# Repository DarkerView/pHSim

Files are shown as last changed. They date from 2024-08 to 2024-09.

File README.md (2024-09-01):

# An Open Source pH Probe Simulator
pH measurement is a quirky and often frustrating technology. Usually working well, they can go wrong in so many ways. With dozens upon dozens of pH probes in service on the cultivation pads I have now spent a few years attempting to discover all of the ways a pH measurement can go bad.

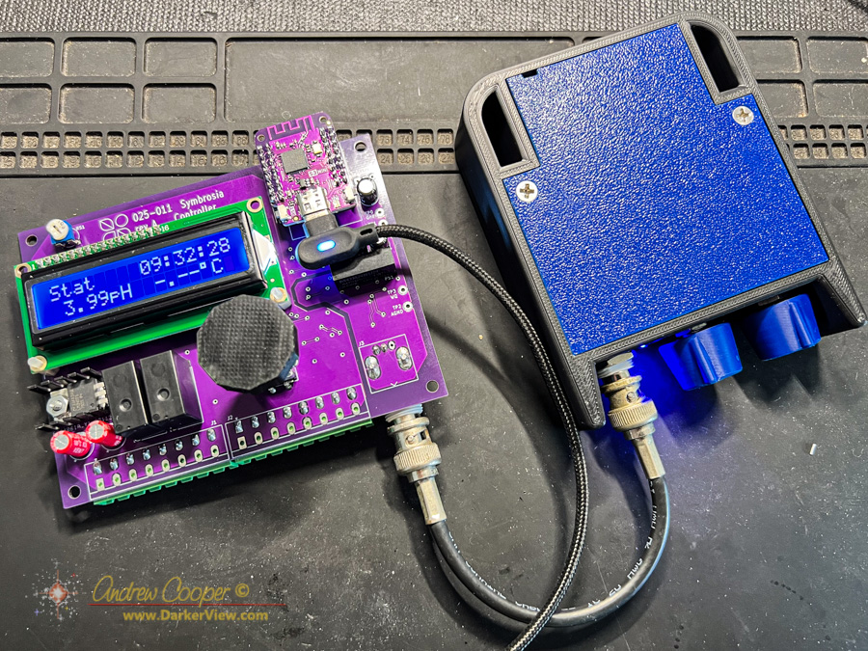
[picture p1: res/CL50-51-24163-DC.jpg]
pH Simulator in use testing a PBR controller


A voltage generated by [ion exchange across a glass membrane](https://atlas-scientific.com/blog/how-does-a-ph-probe-work/) is the magic that makes a pH probe work, simply measure the voltage and you can measure the [hydrogen ion activity of a solution](https://en.wikipedia.org/wiki/PH). The result is a number from 0 to 14, with numbers less than seven being acid, and numbers above seven being basic. Most life, such as healthy algae require conditions close to 7, or neutral, too acid or too basic and everything dies.

While the [voltage generated by the movement of hydrogen ions](https://www.hamiltoncompany.com/process-analytics/ph-and-orp-knowledge/ph-probe-operation-principles) is reasonably large, plus or minus half a volt, it generates only a miniscule current, a few nanoamps. This tiny current makes pH a [challenge to measure](https://en.wikipedia.org/wiki/PH_meter), requiring careful circuitry design in the pH meter. The small current also makes the signal easy to disrupt, a corroded contact, a little salt in a connector, or a damaged cable and it so easily goes awry.

The issue is usually a bad probe, though sometimes it is not. Corroded connectors are a common issue around salt water. In one case I had a cheap, and noisy power supply corrupting the readings. The other issue I face is probes that cannot be removed from the bioreactors once the reactor is full of a thousand liters of saltwater and algae. Thus confirming a bad probe versus another issue is even more critical.

Another problem has popped up on me… When the cultivation folks attempt to re-calibrate a failing probe it can result in bad calibration values entered into the pH instrument even once the offending probe has been replaced. Most instruments do not provide a way to view or reset these bad values. The result is even stranger behavior of the system and a very confused operator, then an equally confused engineer who gets called out to fix it.

My answer to these issues was to make myself a pH simulator, a little box that simulates an ideal pH probe. The actual device is electrically very, very simple… Some voltage references and a few resistors to simulate the voltages of a good pH probe.

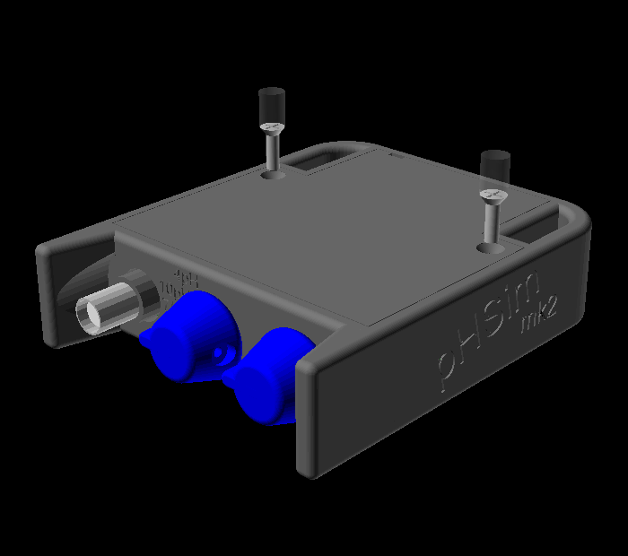
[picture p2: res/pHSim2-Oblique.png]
pH Simulator model


With this simulator I can disconnect the probe and test the pH meter separately, or recalibrate the instrument against an ideal simulated pH probe. The result is easy confirmation of a bad probe, a bad pH meter, or bad cabling. The simulator is also the ideal tool for testing or fixing a pH meter.

While the circuit design may be quite simple, it becomes a fun exercise to design a usable solution around it. First is to house the circuit in a rugged case that can withstand being thown in a toolbag or bounced off the concrete. This case is of course 3D printed from ABS plastic resulting in a solid housing that can take a bit of abuse. Add a proper printed circuit board and you have a neat solution that is pretty close to a commercial product.

No this device does not replace the need to calibrate with the actual pH probe you will be using.  This is an ideal probe, the real pH probe you will be using is less than ideal, compensating for that is what pH calibration is about.

Yes, commercially available pH simulators are out there, [for a thousand dollars](https://www.thomassci.com/Instruments/Electrodes-pH/_/pH-Simulator) or more. Aquaculture operations are quite often low budget startups, so low cost alternatives for useful tools make sense. Thus I am publishing the plans for the unit I originally designed and constructed for my own use.

I have chosen to release the device as a [Creative Commons non-commercial license CC BY-NC 4.0](/LICENSE.md), as this prohibits others from selling or profiting from the device but allows anyone to copy and use as long as they do not sell it for a profit.

As PCB’s are surprisingly cheap these days I have had a small stack of boards made and intend to give a few away to some folks I work with around [NELHA](https://nelha.hawaii.gov/). If you are interested in a PCB, or a kit of parts feel free to contact me.

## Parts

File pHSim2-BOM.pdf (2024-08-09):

# pHSim2 Bill of Materials

Item Description | Manuf | Part | Distributor | Cost | Qty | Exp
C1 | | Nichicon | UHV1V101MED | Digikey | $0.291 | 1 | $0.29
Würth Elektronik 860010573007 | Digikey | $0.150
| | Kemet | C1206C103M5RAC7800 | Digikey | $0.102 | 4 | $0.41
Würth Elektronik 885012208081 | Digikey | $0.115
| | Stackpole | CML1206X7R103KT50V | Digikey | $0.120
| | Yageo | CC1206KRX7R9BB103 | Digikey | $0.138
D1 | | Diodes Inc | S1A-13-F | Digikey | $0.172 | 1 | $0.17
| | Vishay | S1A-E3 | Digikey | $0.248
D2 | Würth Elektronik 151033BS03000 | Digikey | $0.260 | 1 | $0.26
| | Inolux | INL-3AB30 | Digikey | $0.279
J3 | | TE Connect | CONBNC002 | Digikey | $2.120 | 1 | $2.12
| | Adam | RF1-01K-D-00-50-BK-HDW | Digikey | $2.340
| | Stackpole | RMCF1206FT10K0 | Digikey | $0.024 | 4 | $0.10
| | Bourns | CR1206-FX-1002ELF | Digikey | $0.028
| | Yageo | RC1206FR-0710KL | Digikey | $0.038
| | Vishay Dale | CRCW120610K0FKEA | Digikey | $0.048
| | Stackpole | RNCP1206FTD1K00 | Digikey | $0.024 | 3 | $0.07
| | Bourns | CR1206-FX-1001ELF | Digikey | $0.028
| | Yageo | RC1206FR-071KL | Digikey | $0.038
| | Vishay Dale | CRCW12061K00FKEBC | Digikey | $0.048
R8, R9 | | Bourns | PV36W102C01B00 | Digikey | $1.550 | 2 | $3.10
| | TT Electronics | 67YR1KLF | Digikey | $1.690
| | Bourns | 3296Y-1-102LF | Digikey | $2.130
R10, R11 | | Stackpole | RMCF1206FT330R | Digikey | $0.024 | 2 | $0.05
| | Yageo | RC1206FR-07330RL | Digikey | $0.038
| | Bourns | CR1206-FX-3300ELF | Digikey | $0.044
| | Vishay Dale | CRCW1206330RFKEAC | Digikey | $0.045
R12, R13 | | Stackpole | RMCF1206FT20K0 | Digikey | $0.024 | 2 | $0.05
| | Bourns | CR1206-FX-2002ELF | Digikey | $0.028
| | Yageo | RC1206FR-0720KL | Digikey | $0.038
| | Vishay Dale | CRCW120620K0FKEAC | Digikey | $0.045
R14 | 10kΩ potentiometer | Alps Alpine | RK0971110D88 | Digikey | $3.670 | 1 | $3.67
R15, R16 | | Stackpole | RMCF1206FT10M0 | Digikey | $0.030 | 2 | $0.06
| | Yageo | RC1206JR-0710ML | Digikey | $0.035
| | Bourns | CR1206-JW-106ELF | Digikey | $0.046
| | Vishay Dale | CRCW120610M0FKEA | Digikey | $0.048
SW2 | 2P4T rotary switch | Alpha | SR10010F-0204-20F0B-C7-N-0027 | Mouser | $0.000 | 1 | $0.00
TP0, TP1 Test point | Keystone | 5263 | Digikey | $0.198 | 2 | $0.40
| | Keystone | 5267 | Mouser | $0.190
U1 | | TI | LM324LVIDR | Digikey | $0.299 | 1 | $0.30
| | ST | LM324DT | Digikey | $0.333
| | Onsemi | LM324EDR2G | Digikey | $0.350
U2, U3 | | TI | TL431QDR | Digikey | $0.308 | 2 | $0.62
| | ST | TL431CDT | Digikey | $0.358
| | On Semi | TL431ACDR2G | Digikey | $0.439
PCB | pHSim2 PCB | | | JLCPCB | $1.187 | 1 | $1.19
Total | $12.84

### Notes - Pricing as of May, 2024

- Pricing for a quantity of 10 assemblies, prices increase dramatically for lower quantities
- Additional manufacturer and parts numbers listed under the same item are alternate sources

Electrolytic capacitor,
100uF 35V 6x12mm

C2, C3,
C4, C5

Ceramic capacitor, 10nF
50V 1206

Rectifier diode, 50V 1A
SMA

BNC connector, PCB
mount RA

R1, R2,
R6, R7

10.0kΩ 1% resistor,
1/4W 1206

R3, R4,
R5

1.00kΩ 1% resistor,
1/4W 1206

1kΩ trimpot, 20 turn, top
adjust

330Ω 1% resistor, 1/4W
1206

20.0kΩ 1% resistor,
1/4W 1206

10MΩ 5% resistor, 1/4W
1206

LM324 quad opamp,
SOIC14

TL431 voltage reference,
SOIC8

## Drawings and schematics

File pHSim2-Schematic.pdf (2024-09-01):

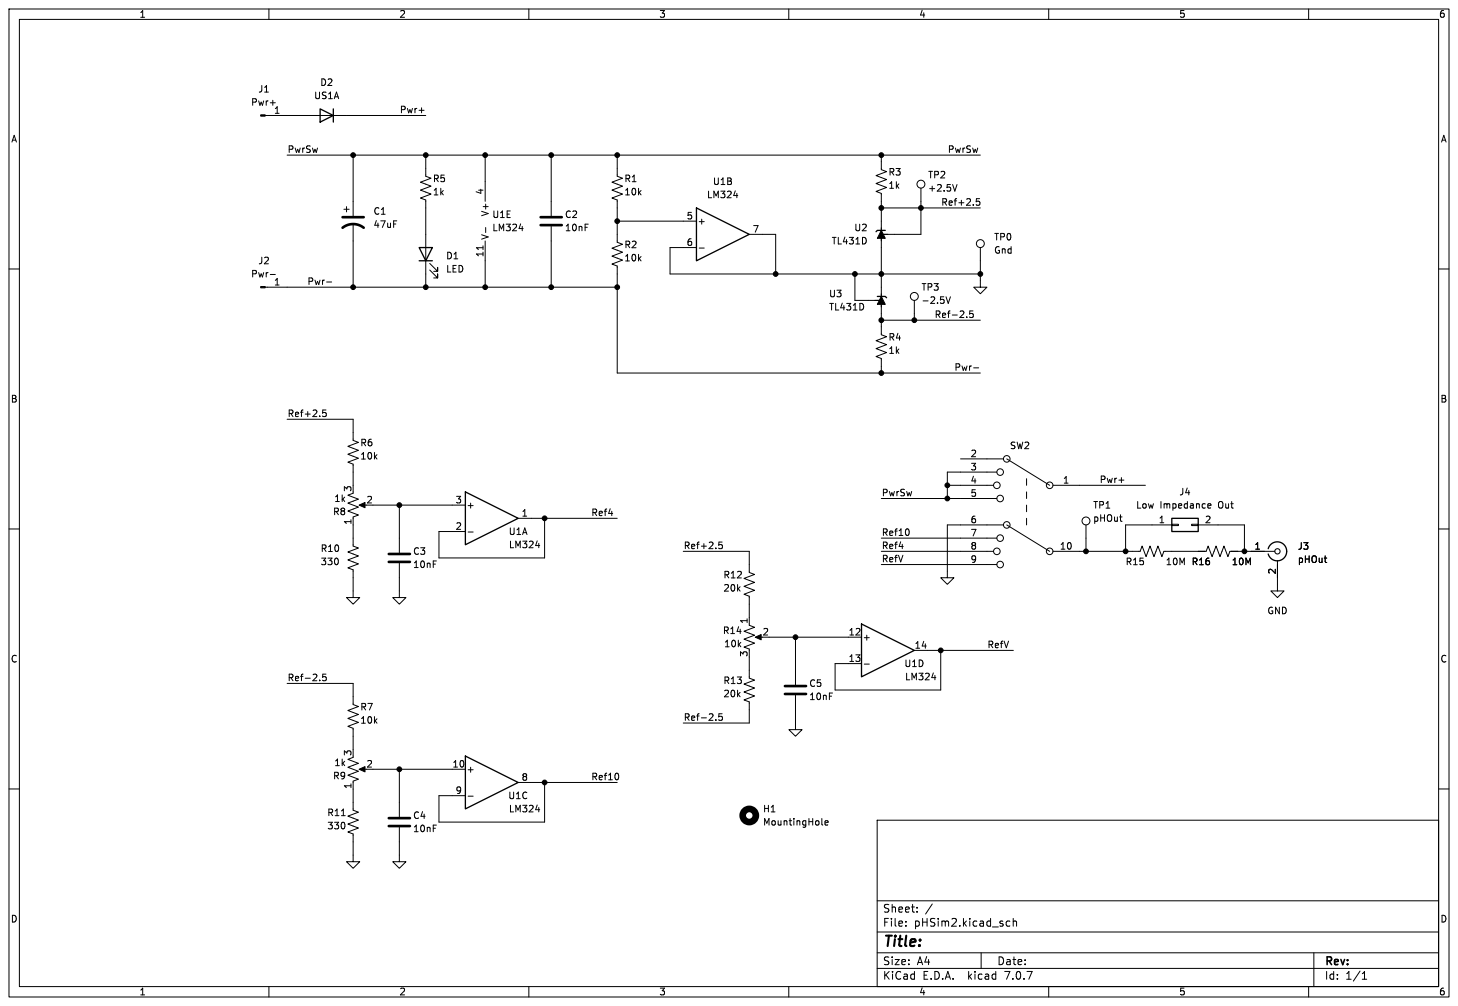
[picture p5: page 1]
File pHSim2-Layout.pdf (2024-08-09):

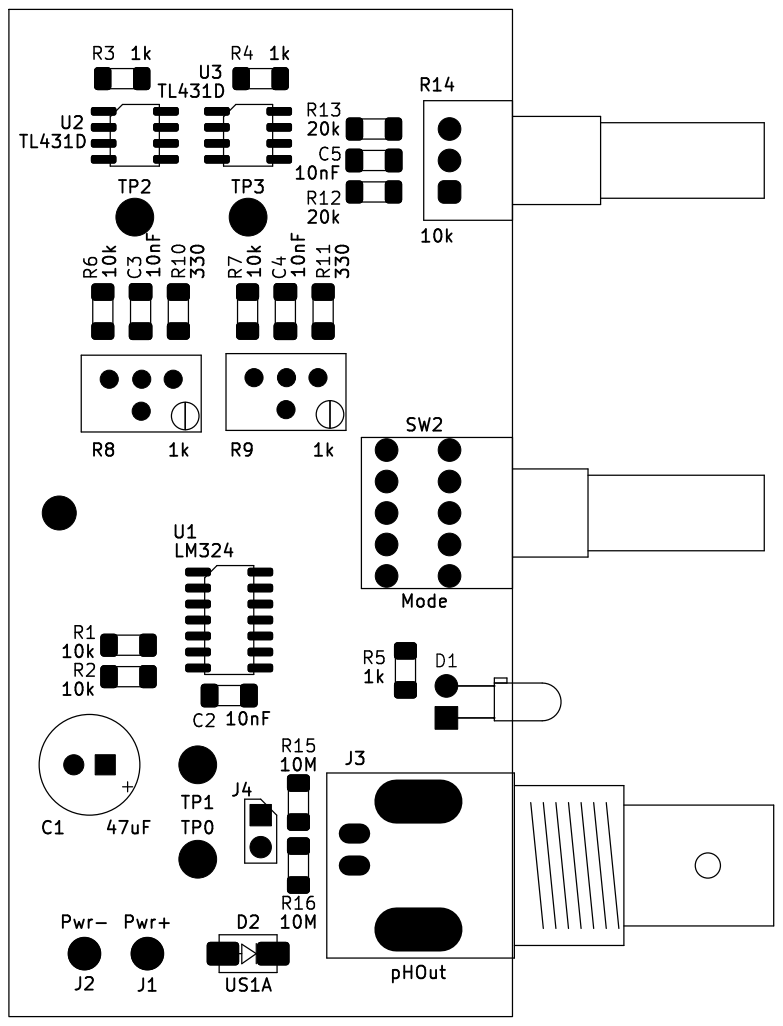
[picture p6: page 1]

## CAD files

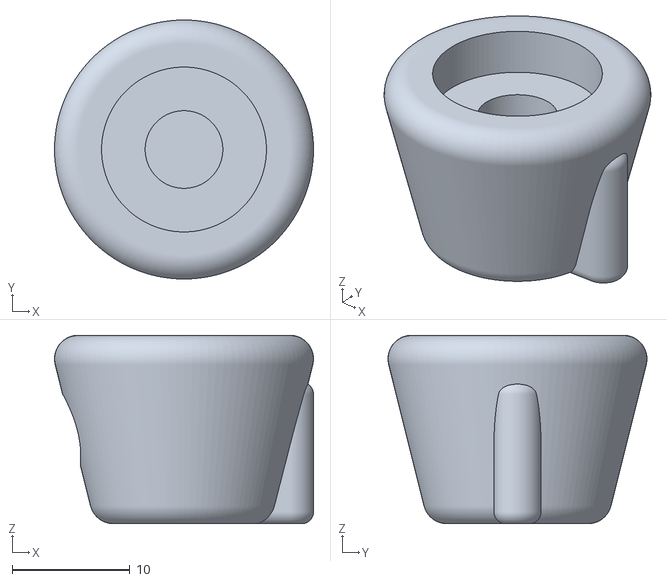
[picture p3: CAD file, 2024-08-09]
stl/pHSim2 Knob.stl
22.0 x 22.0 x 16.0

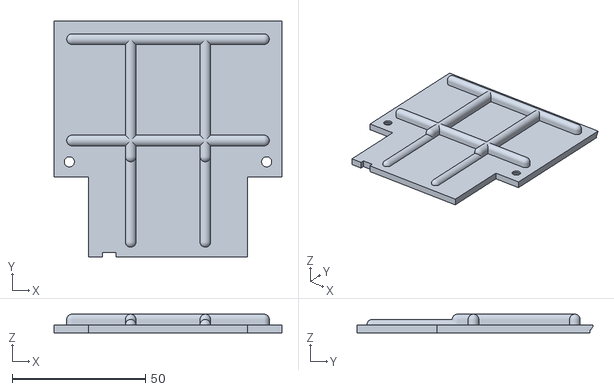
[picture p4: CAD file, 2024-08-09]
stl/pHSim2 Cover.stl
85.5 x 88.6 x 7.00
